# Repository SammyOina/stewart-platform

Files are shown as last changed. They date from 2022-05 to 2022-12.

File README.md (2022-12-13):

# Stewart Platform Force Balance

## Description
With the current developments around the NASA Artemis program, there has been an increased interest in the technologies around rocketry and other STEM subjects. One of the key areas around aerodynamics and specifically for this project is wind tunnel testing. Wind tunnels are commonly used in the automotive and aeronautical industries to verify mathematical model. Simulation and analysis of scaled models is an important step in the development of aircraft, vehicles and other machines since it provides aerodynamic performance data that can be used to inform any modifications or improvements. Such improvements can be aimed toward making the aircraft or vehicles more efficient or safer.

Wind tunnels simulate the behaviour of models in the presence of airflow thus allowing us to obtain the components that better define this interaction i.e. forces and moments. A force balance is consequently used in conjunction with wind tunnels to measure these these forces and moments.  Such force balances are made possible by use of sensors for data acquisition by a computer. The force balance can be 3-component or 6-component; external or internal force balance. Whereas the force balances give very accurate results, some are expensive to build and use.This is especially true in low income countries and it limits technological development in these areas.  Moreover, some objects require complex manoeuvre simulations to imitate the actual
movements in air. There is therefore the need for a solution that can achieve dynamic positioning of objects in the wind tunnel while at the same time obtaining force and moment measurements.

Our project intends to bridge this gap by the use of a low cost six degrees-of-freedom (DOF) Stewart platform as a force balance. This type of force balance will be able to position models in the wind tunnel with six degrees of freedom as well as measure six components of aerodynamic forces (drag, lift and side) and moments (pitching, rolling and yawing). The desired effect is to reduce the barrier of entry for such technology and inspire a generation of engineers who can contribute to the space and automotive industries. 

Using the Stewart platform as a force sensor requires the actuators to be locked with zero degrees of freedom. Instrumentation of the Stewart platform legs by use of strain gauges results in a force balance. Four strain gauges are attached to each leg in a Wheatstone bridge configuration, allowing the leg to act as a force sensor. There is an output every time the leg is under axial loading which is first amplified before being read. HX711s are used for analog to digital conversion of the input. Inverse kinematics is used to give various servo angles for the platform positioning. The project uses IBM cloud IoT platform to connect to our designed PCB used to control the platform and take measurements. The data is delivered to our dashboard running on IBM’s code engine which also allows us to send commands to the PCB as well. 

## What's the problem?
The high cost of wind tunnel force balances limits educational access to study areas around the scientific study in aerodynamics for aeronautical and automotive applications. Lowering the cost of force balances would increase access to studies in these fields and inspire students to participate in STEM, especially in low-income areas/countries.

## Video
[Demo video](https://youtu.be/RzLx-dEQbK0)
## Architecture 

## running
### run dashboard
`cd HMI` \
`go run main.go`

## Walkthrough

## Contributing

## Authors
- [Sammy Kerata Oina](https://www.linkedin.com/in/sammy-oina-b1774110b/)
- [Mogire Earl Spencer](https://www.linkedin.com/in/earl-spencer-b03056204//)

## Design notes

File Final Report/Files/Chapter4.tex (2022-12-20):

\section{Results and Discussion}
\subsection{Six DOF Stewart Platform}
As earlier mentioned, the Stewart platform has already been designed and fabricated and our part in this work was to do an evaluation of the same to verify its mechanical feasibility. As such, the various parts of the platform were obtained and assembled. For further analysis, a 3D model of the same platform was done using Autodesk Inventor.

The assembled Stewart platform is as shown in figure \ref{fig}. Figure \ref{fig1} shows the Stewart platform configuration setup with the Wind tunnel's test section.
\begin{center}
	\begin{figure}[H]
		\centering
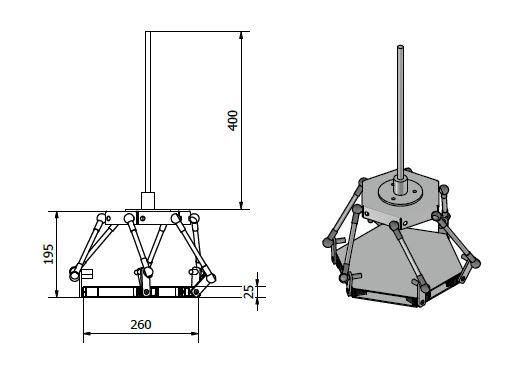
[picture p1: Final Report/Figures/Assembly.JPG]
		
		\caption[Assembled Platform]{Assembly of Stewart Platform}
		\label{fig}
	\end{figure}
\end{center}
\begin{figure}[!htb]%
	\centering
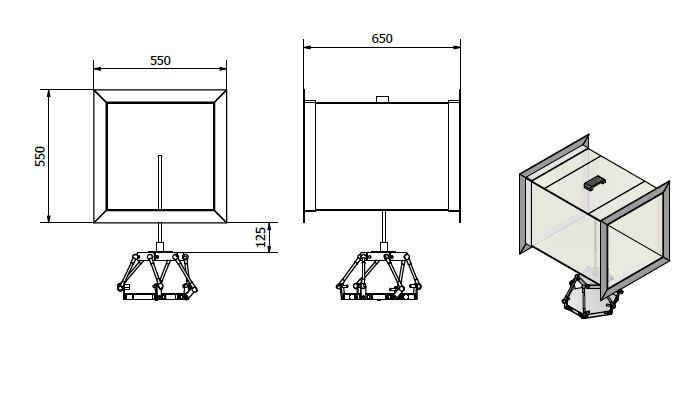
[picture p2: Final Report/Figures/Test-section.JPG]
	\subfloat[\centering Design]{{ }}%
	\qquad
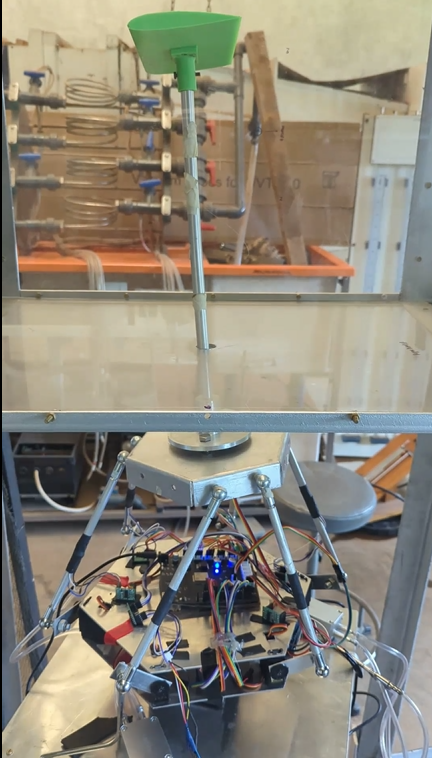
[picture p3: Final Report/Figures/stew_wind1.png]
	\subfloat[\centering Model placement in test section]{{}}
	\caption[Stewart Platform and Test Section]{Stewart platform and Test section configuration}%
	\label{fig:result}%
\end{figure}

\subsection{Strut}
Computational Fluid Dynamics was done for various values of air speed and the following drag forces were
determined from the simulations.
\begin{table}[H]
	\caption{CFD Results}
	\end{table}
	\begin{center}
	\begin{tabular}{|l|l|}
	\hline
	\textbf{Air Velocity(m/s)} & \textbf{Drag Force (N)}\\
	\hline
	10 & 1.203 \\
	\hline
	10 & 6.838 \\
	\hline
	30 & 8.068 \\
	\hline
	40 & 11.367 \\
	\hline
	\end{tabular}
\end{center}
Figure \ref{cfd} shows the effect of the strut to air flow.
\begin{center}
	\begin{figure}[H]
		\centering
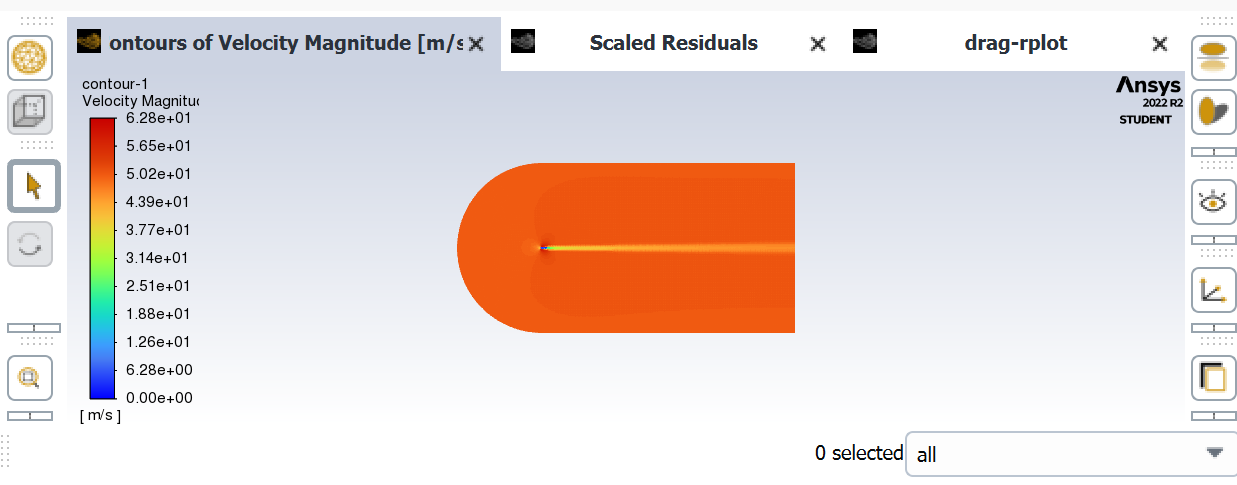
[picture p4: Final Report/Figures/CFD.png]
		
		\caption[CFD]{Computational Fluid Dynamics showing the effect of the strut to air flow}
		\label{cfd}
	\end{figure}
\end{center}

\subsection{Force Measurement by the Stewart Platform}
A static analysis test was performed and the following results were obtained:
\begin{table}[H]
	\caption{FEA Results}
\end{table}
\begin{center}
	\begin{tabular}{|l|l|l|}
		\hline
		\textbf{Name}     & \textbf{Minimum} & \textbf{Maximum} \\
		\hline
		Von Mise's        & 0 MPa            & 63.19 MPa        \\
		\hline
		Displacement      & 0 mm             & 23.74 mm         \\
		\hline
		Safety Factor     & 10.3426 ul       & 15 ul            \\
		\hline
		Equivalent Strain & 0 ul             & 0.052 ul         \\
		\hline
	\end{tabular}
\end{center}
Finite Element Analysis done showed expected strain values on each
Stewart platform leg as shown in figure \ref{strain1}.

\begin{center}
	\begin{figure}[H]
		\centering
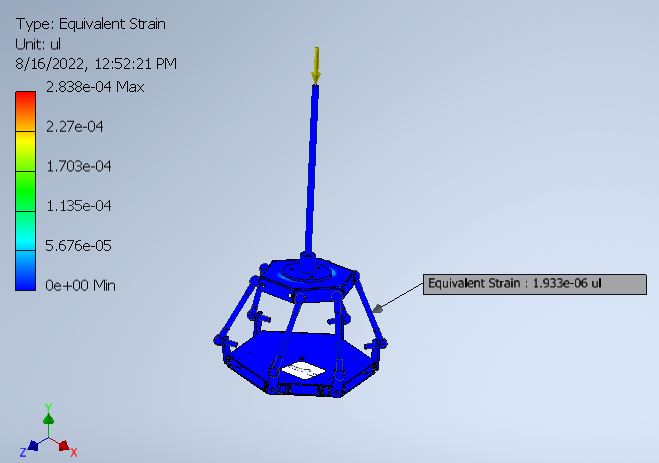
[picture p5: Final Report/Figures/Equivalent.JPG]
		
		\caption[Equivalent strain]{Strain induced on each of the legs}
		\label{strain1}
	\end{figure}
\end{center}
These strains are small and undergo amplification in order provide substantial input for the strain gauges used for force measurements.

\subsection{Human Machine Interface}
The user interface of the platform was programmed using golang and this resulted in the view below with the use of sliders for platform positioning and buttons to set model orientations and start data collection.
\begin{center}
	\begin{figure}[H]
		\centering
		
		\caption[HMI Dashboard]{HMI Dashboard}
	\end{figure}
\end{center}

The top bar of the user interface includes slider buttons to control platform orientation and commands around recording data and calibration as shown in figure \ref{fig:hmi_top}.
\begin{center}
	\begin{figure}[H]
		\centering
		
		\caption[HMI Top Bar]{HMI Top Bar}
		\label{fig:hmi_top}
	\end{figure}
\end{center}

The menu bar also provides options to test the six degrees of freedom for the whole platform as shown in figure \ref{fig:hmi_menu}.
\begin{center}
	\begin{figure}[H]
		\centering
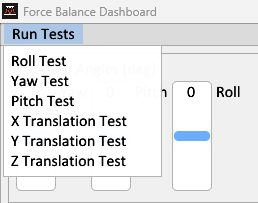
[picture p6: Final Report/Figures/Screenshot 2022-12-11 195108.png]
		
		\caption[HMI menubar]{HMI menubar}
		\label{fig:hmi_menu}
	\end{figure}
\end{center}
A calibration window is also included that is used to set the calibration factor for measurements taken as shown in figure \ref{fig:hmi_calib}
\begin{center}
	\begin{figure}[H]
		\centering
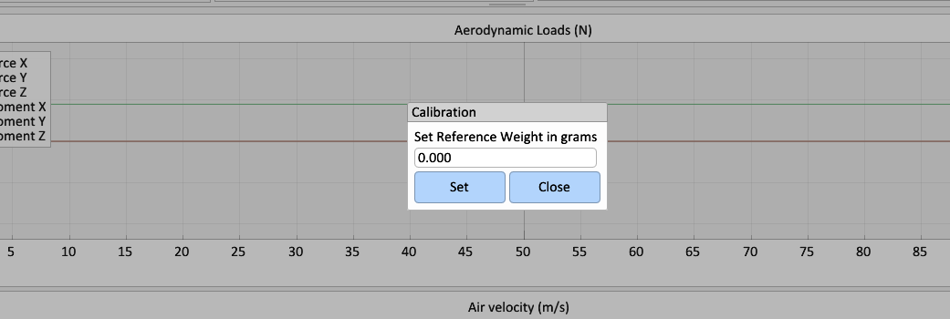
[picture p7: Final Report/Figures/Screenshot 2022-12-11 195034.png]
		
		\caption[HMI calibration]{HMI calibration}
		\label{fig:hmi_calib}
	\end{figure}
\end{center}
The incoming sensor data was also displayed on the screen as shown in the following figures:
\begin{center}
	\begin{figure}[H]
		\centering
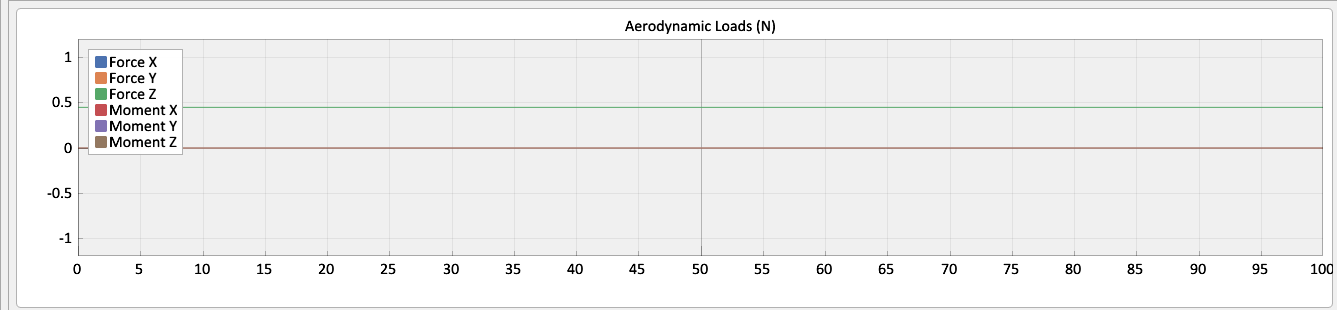
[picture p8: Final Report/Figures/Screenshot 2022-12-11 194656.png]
		
		\caption[HMI Aerodynamic loads]{HMI Aerodynamic loads}
	\end{figure}
\end{center}
\begin{center}
	\begin{figure}[H]
		\centering
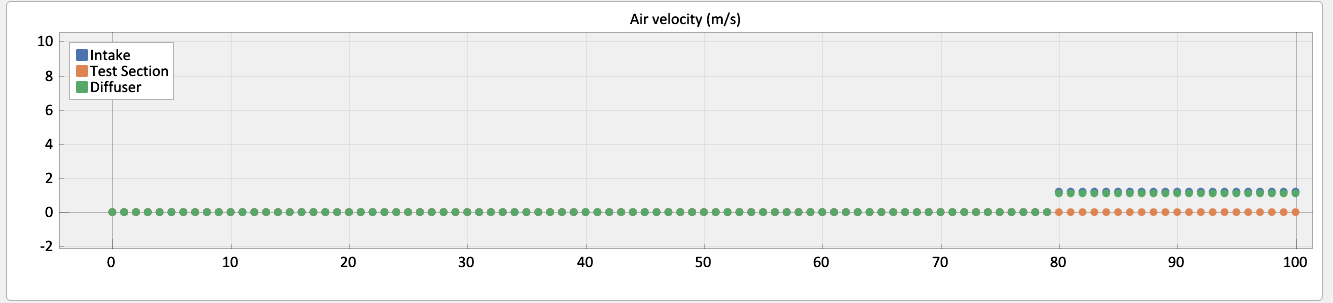
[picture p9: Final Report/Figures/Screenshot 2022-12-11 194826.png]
		
		\caption[HMI Air velocity]{HMI Air velocity}
	\end{figure}
\end{center}
\begin{center}
	\begin{figure}[H]
		\centering
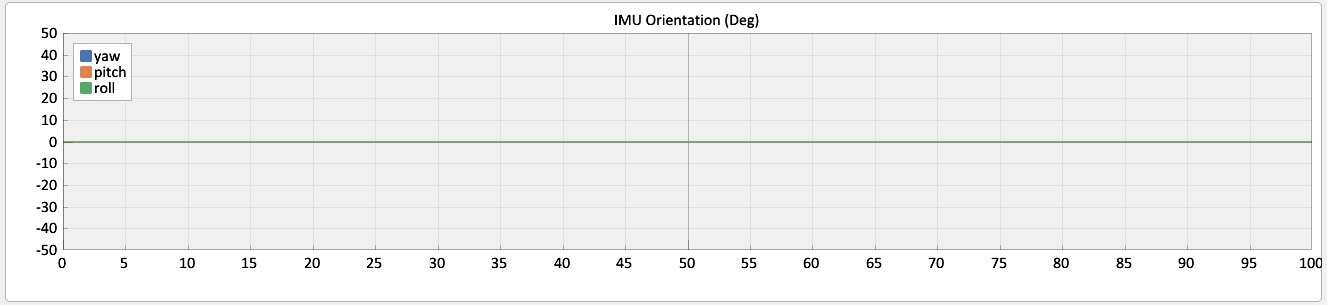
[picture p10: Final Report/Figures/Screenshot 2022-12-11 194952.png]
		
		\caption[HMI IMU readings]{HMI IMU readings}
	\end{figure}
\end{center}
\begin{center}
	\begin{figure}[H]
		\centering
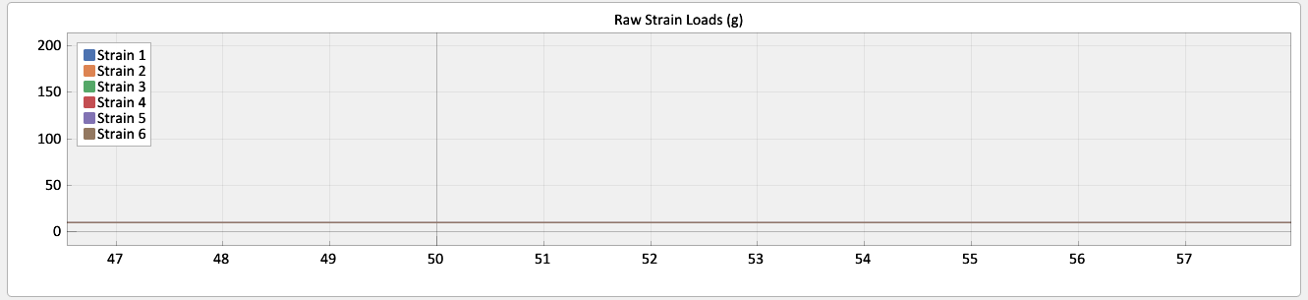
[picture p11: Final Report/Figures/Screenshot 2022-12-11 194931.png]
		
		\caption[HMI Raw Strain]{HMI Raw Strain}
	\end{figure}
\end{center}
\subsection{PCB}
The schematics from the electrical designs as seen in the appendix were routed to generate a PCB ready for manufacture. The fabricated PCB is shown in figure \ref{fig:pcb_fab}
\begin{center}
	\begin{figure}[H]
		\centering
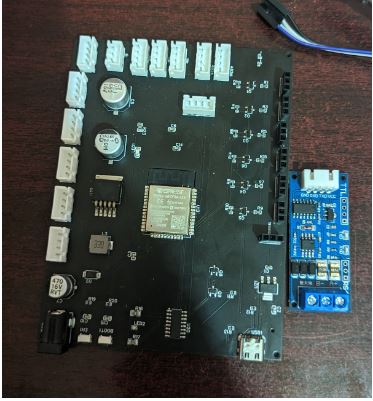
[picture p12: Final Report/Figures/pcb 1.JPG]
		
		\caption[Printed Circuit Board view]{Printed Circuit Board}
		\label{fig:pcb_fab}
	\end{figure}
\end{center}
The PCB is compact as shown in the figure \ref{fig:pcb_fab}. It is also integrates most of the components to minimize use of wires to make connections.

\subsection{Smoke Visualization}
\subsubsection{Smoke Rake}
The smoke rake was 3D printed at iPIC and assembled with its lid as shown.
\begin{figure}[!htb]%
	\centering
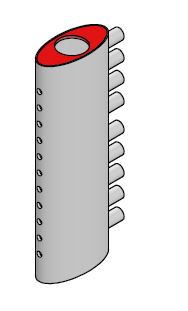
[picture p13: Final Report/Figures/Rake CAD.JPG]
	\subfloat[\centering Smoke Rake CAD]{{ }}%
	\qquad
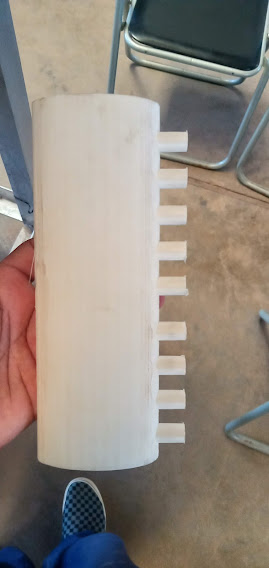
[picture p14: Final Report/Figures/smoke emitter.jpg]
	\subfloat[\centering 3D Printed Rake]{{}}
	\caption[3D Printed rake]{Smoke rake and lid assembled}%
	\label{fig:result}%
\end{figure}
\subsubsection{Smoke Rake and Pipe Assembly}
The Smoke rake was assembled with a metal pipe for rigid support and also for smoke introduction into the
smoke rake as shown.
\begin{figure}[!htb]%
	\centering
	\subfloat[\centering CAD Assembly]{{ }}%
	\qquad
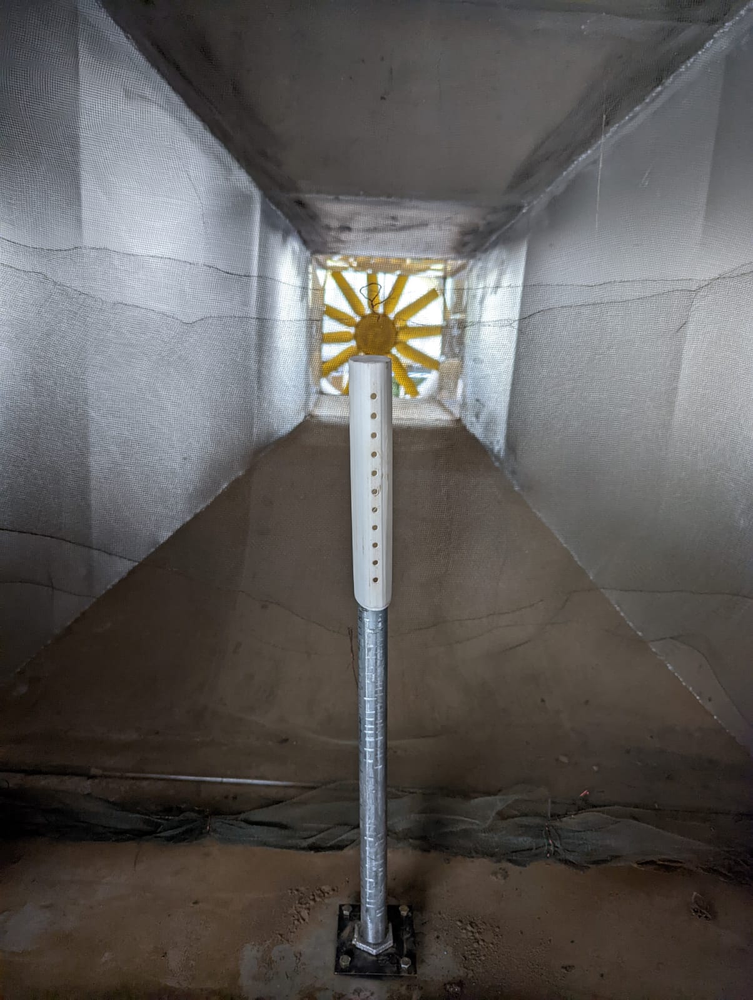
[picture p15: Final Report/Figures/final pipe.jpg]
	\subfloat[\centering Final Part]{{}}
	\caption[Final rake and pipe]{Smoke rake and pipe assembly and setup in the wind tunnel}%
	\label{fig:result1}%
\end{figure}
\subsection{Model Testing}
An aerodynamic model was subjected to wind tunnel testing and values of forces and moments were collected
using the Stewart platform force balance. The tests were done at 0 angle of attack, and at a speed of 3m/s.
The following results were obtained.
\begin{figure}[!htb]%
	\centering
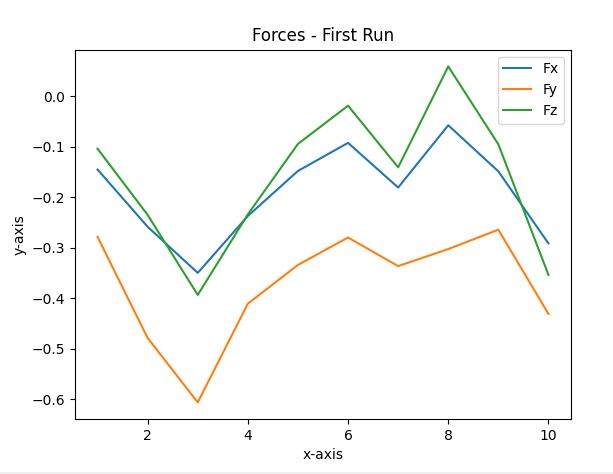
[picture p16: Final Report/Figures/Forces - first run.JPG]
	\subfloat[\centering First run]{{ }}%
	\qquad
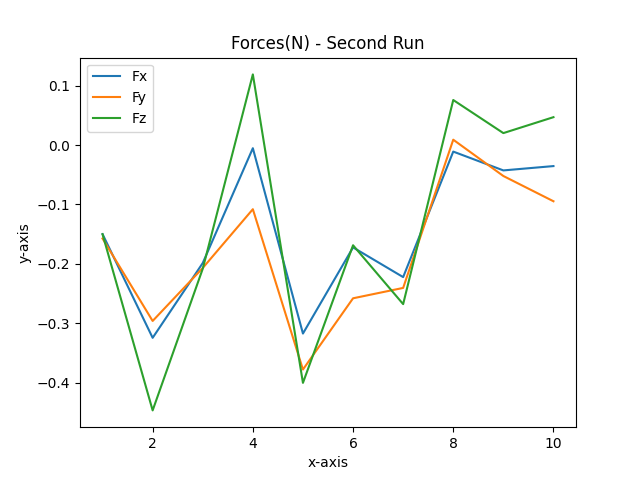
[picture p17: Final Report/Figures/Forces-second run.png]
	\subfloat[\centering Second run]{{}}
	\caption[Force values for first and second run]{Force values for first and second run}%
	\label{fig:result1}%
\end{figure}
\begin{center}
	\begin{figure}[H]
		\centering
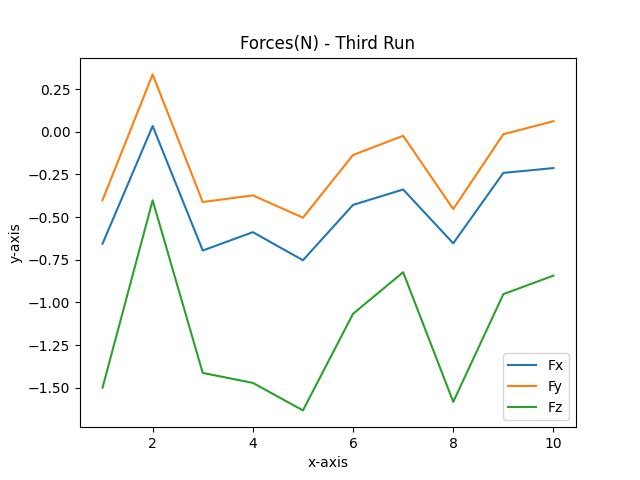
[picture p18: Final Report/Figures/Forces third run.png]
		
		\caption[Forces Third run]{Forces obtained form the third run}
		\label{fig:pcb_fab}
	\end{figure}
\end{center}
%\begin{figure}[!htb]%
%	\centering
%	\subfloat[\centering First run]{{\includegraphics[width=8cm]{Figures/Moments_first_run.png} }}%
%	\qquad
%	\subfloat[\centering Second run]{{\includegraphics[width=8cm]{Figures/Moments_second_run.png}}}
%	\caption[Moment values for first and second run]{Moment values for first and second run}%
%	\label{fig:result1}%
%\end{figure}
%\begin{center}
%	\begin{figure}[H]
%		\centering
%		\includegraphics[width=0.7\linewidth]{Figures/Moments third run.png}
%		\caption[Moments from Third run]{Moments obtained form the third run}
%		\label{fig:pcb_fab}
%	\end{figure}
%\end{center}
\subsection{Discussion}
The Stewart platform is able to position models in various dynamic positions depending on the angle values
of yaw, roll and pitch as well as the amount of displacements in the x-, y- and z-directions input via the HMI.
 Application of load on the platform
subjects each of the legs to axial forces which causes strain. This strain can be used to determine aerodynamic forces
on models during wind tunnel testing. However, aerodynamic forces due to the strut must be put to account because from
simulations, drag forces are developed by the strut when there is airflow. Smoke introduced into the wind tunnel allows
visualization of airflow around a model. Pitot tube probes used and their transducers provide valuable information used 
in post analysis to determine the aerodynamic coefficients (drag, lift).

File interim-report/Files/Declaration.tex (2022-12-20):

\addcontentsline{toc}{section}{Declaration}
\section*{Declaration}

We hereby declare that the work contained in this report is original; researched and documented by the undersigned students. It has not been used or presented elsewhere in any form for award of any academic qualification or otherwise. Any material obtained from other parties have been duly acknowledged. We have ensured that no violation of copyright or intellectual property rights have been committed.
\begin{enumerate}
	\item Sammy Kerata Oina\vspace*{.2cm}\\
	Signature\ldots\ldots\ldots\ldots\ldots\ldots\ldots\ldots\ldots\ldots Date\ldots\ldots\ldots\ldots\ldots\ldots\ldots\ldots\ldots\ldots
	\item Earl Spencer Mogire\vspace*{.2cm}\\
	Signature\ldots\ldots\ldots\ldots\ldots\ldots\ldots\ldots\ldots\ldots Date\ldots\ldots\ldots\ldots\ldots\ldots\ldots\ldots\ldots\ldots
\end{enumerate}

\vspace*{.5cm}
Approved by supervisors:
\begin{enumerate}
	\item Dr. Anthony K. Muchiri \vspace*{.2cm}\\
	Signature\ldots\ldots\ldots\ldots\ldots\ldots\ldots\ldots\ldots\ldots Date\ldots\ldots\ldots\ldots\ldots\ldots\ldots\ldots\ldots\ldots
	%\item Prof. George N. Nyakoe\vspace*{.2cm}\\
	%Signature\ldots\ldots\ldots\ldots\ldots\ldots\ldots\ldots\ldots\ldots Date\ldots\ldots\ldots\ldots\ldots\ldots\ldots\ldots\ldots\ldots
	%\item Ms. Maurine Andanje\vspace*{.2cm}\\
	%Signature\ldots\ldots\ldots\ldots\ldots\ldots\ldots\ldots\ldots\ldots Date\ldots\ldots\ldots\ldots\ldots\ldots\ldots\ldots\ldots\ldots
\end{enumerate}

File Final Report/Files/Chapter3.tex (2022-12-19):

\section{Methodology}
\subsection{Outline}
This section will look into:
\begin{itemize}
	\item Mechanical Design:
	\item Electrical Design
	\item Instrumentation
	\item Software and Control Design
\end{itemize}

\subsection{Mechanical Design}
\subsubsection{Inverse Kinematics of a Stewart Platform}
This is the calculation of each leg length based on the desired position of the Stewart platform.
For the Stewart platform, the translation $^{p}T_{b}$ from the base origin to the platform origin can be described with a single vector T = $(t_{x} t_{y} t_{z})^{T} $. The rotation of the platform can be denoted as $^{p}R_{b}$. Thus the following relationship for the frame of reference can be stated \cite{Eisele_2019}:
\begin{ceqn}
	\begin{align}
		^{p}T_{b} = T
	\end{align}
\end{ceqn}
\begin{ceqn}
	\begin{align}
		^{p}R_{b} = R
	\end{align}
\end{ceqn}
\begin{ceqn}
	\begin{align}
		^{b}T_{p} =(^{p}T_{b})^{-1} =T^{-1}
	\end{align}
\end{ceqn}
\begin{ceqn}
	\begin{align}
		^{b}R_{p} = (^{p}R_{b})^{-1}
	\end{align}
\end{ceqn}
\begin{center}
	\begin{figure}[!h]
		\centering
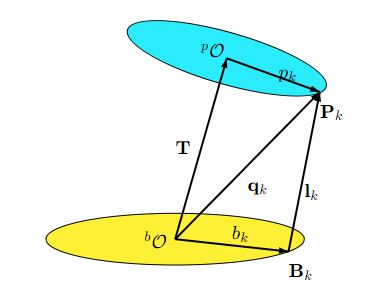
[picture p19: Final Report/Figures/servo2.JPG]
		
		\caption[Leg length]{Leg Length \cite{Eisele_2019}}
	\end{figure}
\end{center}
The leg length $l_{k}$ can therefore be found with:
\begin{ceqn}
	\begin{align}
		l_{k} = P_{k} - B_{k} = T + R \times p \times R^{-1} - b_{k}
	\end{align}
\end{ceqn}
Where,\\
$P_{k}$ - leg attachment on platform \\
$B_{k}$- leg attachment on base
\subsubsection{Inverse Kinematics Using Rotational Servo Motors}
For a rod of fixed length d between servo horn anchor $H_{k}$ and platform anchor $P_{k}$.  $H_{k}$ has a distance h between the original base anchor and servo shaft $B_{k}$. The vector h is perpendicular to the servo shaft and is rotated by angle $\alpha_{k}$ when lifted from the horizontal line.
\begin{center}
	\begin{figure}[!h]
		\centering
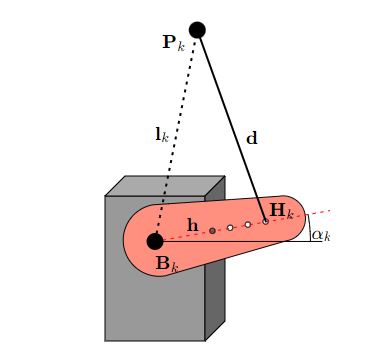
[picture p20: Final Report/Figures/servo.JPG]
		
		\caption[Servo angle]{Servo angle \cite{Eisele_2019}}
	\end{figure}
\end{center}
Further, looking from the top onto the base, each servo can be rotated by the angle $\beta_{k}$ in addition to its position $B_{k}$. The servo shaft $s_{k}$ moves in the x-y plane and is orthogonal to the vector h.
\begin{center}
	\begin{figure}[!h]
		\centering
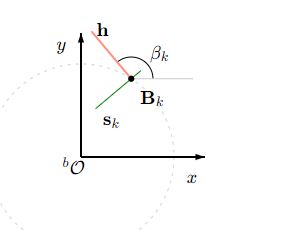
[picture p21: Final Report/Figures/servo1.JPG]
		
		\caption[Planar view]{Planar view \cite{Eisele_2019}}
	\end{figure}
\end{center}
The anchor $H_{k}$ can be calculated as we rotate around the z-axis with angle $\beta_{k}$ and  by $-\alpha_{k}$ around the y-axis to lift the servo horn which lies in the local x-axis \cite{Eisele_2019}.
\begin{ceqn}
	\begin{align}
		H_{k} = B_{k} + R_{z}(\beta_{k}) R_{y}(-\alpha_{k})\begin{pmatrix}
			                                                   |h| \\ 0 \\ 0
		                                                   \end{pmatrix}
		\label{eq:myeqn2}
	\end{align}
\end{ceqn}
\begin{ceqn}
	\begin{align}
		= B_{k} + |h|\begin{pmatrix}
			             cos(\alpha_{k})cos(\beta_{k}) \\
			             cos(\alpha_{k})sin(\beta_{k}) \\
			             sin(\alpha_{k})
		             \end{pmatrix}
		\label{eq:myeqn4}
	\end{align}
\end{ceqn}
Carrying out the same procedure but with the servo arm when it is on the opposite side and we have:
\begin{ceqn}
	\begin{align}
		H_{k} = B_{k} + R_{z}(\beta_{k}) R_{y}(\pi -\alpha_{k})\begin{pmatrix}
			                                                       -|h| \\ 0 \\ 0
		                                                       \end{pmatrix}
		\label{eq:myeqn5}
	\end{align}
\end{ceqn}
\begin{ceqn}
	\begin{align}
		= B_{k} + |h|\begin{pmatrix}
			             cos(\alpha_{k})cos(\beta_{k}) \\
			             cos(\alpha_{k})sin(\beta_{k}) \\
			             sin(\alpha_{k})
		             \end{pmatrix}
		\label{eq:myeqn6}
	\end{align}
\end{ceqn}
Squaring the lengths of h, d, $l_{k}$ we get the relationship:
\begin{ceqn}
	\begin{align}
		h^2 = (H_{k}-B_{k})^{T}(H_{k}-B_{k})
	\end{align}
\end{ceqn}
\begin{ceqn}
	\begin{align}
		d^2 = (P_{k}-H_{k})^{T}(P_{k}-H_{k})
	\end{align}
\end{ceqn}
\begin{ceqn}
	\begin{align}
		l_{k}^2 = (P_{k}-B_{k})^{T}(P_{k}-B_{k})
	\end{align}
\end{ceqn}
From the above relationships, further derivation and trigonometric substitutions are done to obtain the inverse kinematics used to calculate each servo angle. This is given as \cite{Eisele_2019}:
\begin{ceqn}
	\begin{align}
		\alpha_{k} = sin^{-1}(\frac{g_{k}}{\sqrt{e_{k}^2+f_{k}^2}})-arctan2(f_{k}, e_{k})
	\end{align}
\end{ceqn}
Where,
$$e_{k} = 2hl_{k}^{(z)} $$
$$e_{k} = 2h(cos(\beta_{k})I_{k}^{(x)}+sin({\beta_{k}})I_{k}^(y))$$
$$g_{k} = l_{k}^2 - (d^2 - h^2)   $$

\subsubsection{Actuation}
Two methods of actuation are popular with Stewart platforms:
\begin{itemize}
	\item Linear actuators
	\item Use of motors
\end{itemize}
Whereas linear actuators are relatively easy to control, they are very expensive. Thus the choice of motors.

\subsubsection*{Motor Selection}
One parameter was considered in our motor selection i.e. torque required. From the Autodesk Inventor design environment, the mass of the moving platform and mechanical couplings was 2.6kg. Each motor is supposed to move a minimum mass of 0.177kg. Using a servo horn of distance 45mm centre-to-centre, and Distance = $ \pi $ D, then:
\begin{ceqn}
	\begin{align}
		Torque = (0.1777 \times 9.81)\times \frac{141.37}{1000} = 0.246 N\cdot m
	\end{align}
\end{ceqn}
Motors of minimum torque of 0.2 N $\cdot m$ were considered. But for control considerations, only stepper motors and servo motors were shortlisted. Servo motor was considered over Stepper motor because they are cheaper. Also, we are only interested in 0 - 180 degrees positions.

The Servo motor \textbf{TowerPro MG995} is suitable for this project. The specifications provided by the manufacturer are as follows:

\begin{table}[!h]
	\caption[Motor Specifications]{TowerPro MG995 Specifications}
\end{table}
\begin{center}
	\begin{tabular}{|l|l|}
		\hline
		\textbf{Model}                  & TowerPro MG995                \\
		\hline
		\textbf{Operating Voltage}      & 4.8V - 6.6V                   \\
		\hline
		\textbf{Operating Speed @ 4.8V} & 0.20sec/60$^{\circ}$          \\
		\hline
		\textbf{Operating Speed @ 6.6V} & 0.16sec/60$^{\circ}$          \\
		\hline
		\textbf{Stall torque @ 4.8V}    & 9.4 kg-cm or 0.94 N $\cdot$ m \\
		\hline
		\textbf{Stall torque @ 6.6V}    & 11 kg-cm or 1.1 N $\cdot$ m   \\
		\hline
	\end{tabular}
\end{center}
Prices range between \textbf{Ksh.700} and \textbf{Ksh.1400}

The previous servos used for the project were SG5010 which proved not to be able to handle the torque requirements of the platform,
as a result the plastic gears in those servos were destroyed. The replacement of the servos with MG995 solved the problem due to the higher torque capacity and has metal gears.

\subsubsection{Finite Element Analysis}
A Finite Element Analysis was done on the Stewart platform design to determine its performance under given loads. The platform is going to be subjected to a force during wind tunnel testing. A maximum load of 50N was selected for the Finite Element Analysis. This could be more or less since models vary in size. The z-component of the force is considered.
The mesh generated is shown in the figure \ref{fig:feamesh}.
\begin{center}
	\begin{figure}[H]
		\centering
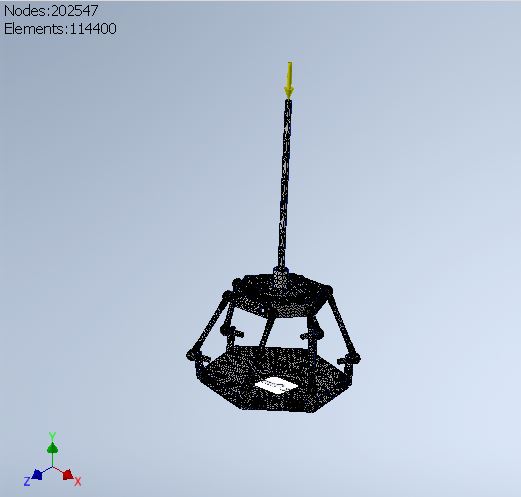
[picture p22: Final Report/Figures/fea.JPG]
		
		\caption[Stewart platform mesh]{Stewart platform mesh}
		\label{fig:feamesh}
	\end{figure}
\end{center}
The rods/legs of the Stewart platform were subjected to axial forces which caused slight strains which can be used to obtain force and moment measurements during wind tunnel testing.
\clearpage
\begin{center}
	\begin{table}[H]
		\caption{Operating Conditions}
		\centering
	\end{table}
	\begin{tabular}{|l|l|}
		\hline
		\textbf{Load Type} & \textbf{Force} \\
		\hline
		Magnitude          & 50.0N          \\
		\hline
		Vector X           & 7.794N         \\
		\hline
		Vector Y           & -48.206N       \\
		\hline
		Vector Z           & 10.745N        \\
		\hline
	\end{tabular}
\end{center}

\begin{center}
	\begin{table}[!h]
		\caption[FEA Setup]{Other FEA setup parameters}
		\centering
	\end{table}
	\begin{tabular}{|l|l|}
		\hline
		Constraint & Fixed                       \\
		\hline
		Materials  & Aluminium 6061              \\
		           & Stainless steel             \\
		\hline
		Contacts   & All bonded                  \\
		\hline
		Mesh       & Avg element size: 0.1mm     \\
		           & Minimum element size: 0.2mm \\
		           & Grading Factor: 1.50        \\
		           & Maximum turn angle: 60 deg  \\
		\hline
	\end{tabular}
\end{center}

\subsection{Strut}
The strut will go into the test section of the Wind tunnel. Consequently, it will be
subjected to the flow forces in the wind tunnel. It has therefore been made of as small diameter as possible.
A computational fluid dynamics test was done to ascertain the magnitude of drag force experienced and the effect that the strut
will have on the flow in the tunnel. The test was done using ANSYS.
\begin{center}
	\begin{table}[!h]
		\caption[CFD Setup]{CFD setup parameters}
		\centering
	\end{table}
	\begin{tabular}{|l|l|}
		\hline
		\textbf{Parameter} & \textbf{Value/Type} \\
		\hline
		Type of test       & Fluid flow (Fluent)         \\
		\hline
		Type of Simulation & Steady State\\
		\hline
		Type of fluid      & air                 \\
		\hline
		Mesh size      &  0.001mm            \\
		\hline
		Growth rate     & default (1.2)             \\
		\hline
		Behavior  & soft             \\
		\hline
		Defeature size      & 5.5902 e-004m               \\
		\hline
		Velocity           & 10 - 40 m/s         \\
		\hline

	\end{tabular}
\end{center}
The speed of air flow in the wind tunnel is variable thus the simulation was done 
using speeds between 10m/s and 40 m/s in steps of 10 m/s.

\subsubsection{Smoke Visualization System}
To implement streamline smoke lines in the wind tunnel, a smoke rake, which is an aerodynamically shaped
body (usually elliptical) featuring a row of tubes through which the smoke exits was designed.
The CAD model was deigned using Autodesk Inventor and the rake was prepared for 3D printing at iPIC
in JKUAT. The rake design is shown in figure \ref{smoke}.
\begin{center}
	\begin{figure}[H]
		\centering
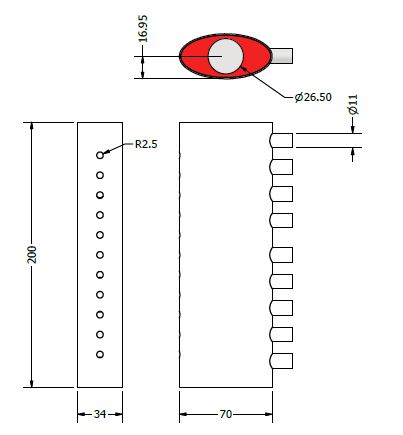
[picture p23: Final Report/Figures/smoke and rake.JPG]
		
		\caption[Smoke Rake]{Smoke rake design}
		\label{smoke}
	\end{figure}
\end{center}
The smoke emitting holes are 6mm in diameter and the air inlet holes are 5mm in diameter.
20mm diameter hole on the lid (color coded red) shown in the  plan view is for metal pipe connection.

\subsubsection*{Smoke Rake and Pipe Assembly}
A metal pipe was used to provide rigid support to the smoke rake in the wind tunnel as well as placing it at the center
(vertically). A pipe of length 400mm and diameter 3/4"(19.05mm) is used. The pipe surface was roughed using a hacksaw in
order to minimize any turbulence in the flow since it was be placed in the intake section. A 1.5mm plate of 10mm by 10mm by
and two plumbing nuts are required to mount the pipe in the intake section. The smoke rake and pipe design is shown
in figure \ref{pipe and rake}
\begin{center}
	\begin{figure}[H]
		\centering
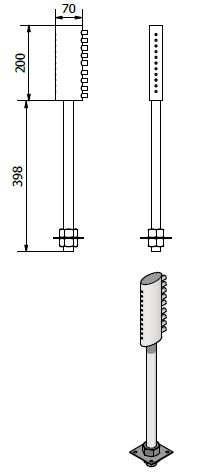
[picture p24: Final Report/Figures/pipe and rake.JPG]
		
		\caption[Pipe and rake]{Pipe and rake assembly design}
		\label{pipe and rake}
	\end{figure}
\end{center}
For the complete assembly, a 20mm diameter hole was drilled on the floor of the wind tunnel at the intake section
and the pipe was held fast to the floor by two plumbing nuts on both sides of the 1.5mm plate. The plate was fastened to
the floor by use of M6 bolts and nuts.
\subsection{Instrumentation}
\subsubsection{Design of the Force Sensor}
The force sensor module was used to measure the force and moments from the aerodynamic loads applied on model 
being tested in the wind tunnel. The forces to be measured are the drag, lift and thrust as well as
 associated moments. For this subsystem two possible conceptual designs were considered:
\begin{itemize}
	\item External force sensor
	\item Stewart Platform as a force sensor
\end{itemize}
\subsubsection*{External Force Sensor}
In this case it would require at least 3 orthogonally positioned load cells measuring each force component. Each load cell would be mechanically linked to the model such that forces experienced on each axis are measured by each load cell as shown in figure \ref{fig:balex}.
\begin{center}
	\begin{figure}[H]
		\centering
		
		\caption[Diagram of a force balance]{Diagram of a force balance \cite{post_force_2010}}
		\label{fig:balex}
	\end{figure}
\end{center}
This configuration is, however, bulky since it requires an additional external system for force measurements in addition to the Stewart platform for positioning the model. This is however complemented by the simplicity in calibration of the load cells and does not require a complex force transformation matrix and other issues with force amplification created by the use of an integrated system.
\subsubsection*{Stewart Platform as a force sensor}
In this configuration, the Stewart platform legs are used as force sensors by attaching strain gauges on the 
legs of platform. Similar work has been done by Ferreira\cite{ferreira2015design} without the use of actuators as is proposed in this project. Using the Stewart platform as a force sensor requires the actuators to be locked with zero degrees of freedom.

Four strain gauges are required for each leg for a full Wheatstone bridge configuration.
\begin{center}
	\begin{figure}[H]
		\centering
		
		\caption[Strain Gauge Configuration]{Strain Gauge Configuration \cite{noauthor_measuring_nodate}}
		\label{strain}
	\end{figure}
\end{center}
In this case, as shown in figure \ref{strain}, the load cells are able to measure the axial strain on each leg. R1 and R3 are active strain gauges measuring the compressive Poisson effect (–νe). R2 and R4 are active strain gages measuring the tensile strain (+e). The output generated from the Wheatstone bridge is then amplified and read to determine the strain on each leg.
In the case of this project, a full bridge strain gauge sensor with each strain gauge orthogonally positioned allowing for elimination of noise and measurement of the strain axially on each rod is used.

\subsubsection*{Force transformation matrix}
The forces experienced at the top of the platform are distributed between the 6 legs and as result, a force transformation matrix is required to resolve the forces applied on each axis as measured by each load cell on each leg.

The forces experienced by the legs can be expressed as:
\begin{ceqn}
	\begin{align}
		\begin{Bmatrix}
			\vec{F}_e \\
			\vec{M}_e \\
		\end{Bmatrix} = [H]\{F\}
	\end{align}
\end{ceqn}

Where
\begin{itemize}
	\item $\vec{F}_e $ - external force applied to the platform
	\item $\vec{M}_e$ - external moment applied to the platform
	\item H - transformation matrix which relates measured forces and applied forces
	\item F - axial force
\end{itemize}
The derivation has been done and is presented in the appendix A.4.

\subsubsection*{Bonding strain gauges}
The strain gauge bonding process began by roughing the bonding surface on the aluminium tubes using sand paper. 
The surface was then cleaned using acetone. Superglue was when applied on the surface followed by the strain gauge while applying pressure on the strain gauge. 
Resin (araldite) was then placed on the strain gauge to provide protection to strain gauge from mechanical damage. 
Jumper wires were then soldered onto the lead wires of the strain gauge as shown in \ref{fig:strain_bond}. 
Finally, the assembly was covered with heat shrinkable tubing.
\begin{center}
	\begin{figure}[H]
		\centering
		
		\caption[Strain gauge bonding process]{Strain gauge bonding process}
		\label{fig:strain_bond}
	\end{figure}
\end{center}

\subsection{Velocity Measurement}
An important part in wind tunnel measurements is the measure of pressure at specific points in the wind tunnel and computing the corresponding air speed. This is achieved by the use of a pitot probe.
\begin{center}
	\begin{figure}[H]
		\centering
		
		\caption[Pitot-static tube]{Pitot-static tube \cite{viquerat_continuous_2006}}
	\end{figure}
\end{center}
For steady flow of an incompressible fluid for which viscosity can be neglected, the fundamental equation has the form\cite{viquerat_continuous_2006}:

\begin{ceqn}
	\begin{align}
		v = \sqrt{\frac{2(P_{0} - P)}{\rho}}
	\end{align}
\end{ceqn}

Where V is the speed of the fluid, $P_{0}$ is the total, also called the stagnation, pressure at that point of measurement, and P is the static pressure at the same point.

\begin{center}
	\begin{figure}[H]
		\centering
		
		\caption[RS485 communication]{RS485 communication}
		\label{fig:rs485}
	\end{figure}
\end{center}
The module communicates to the microcontroller using a TTL to RS485. Each module is individually addressable further simplifying the interface as shown in figure \ref{fig:rs485}.
The protocol allows for long distance serial communication and interface with multiple devices on the same bus.

Three pitot probes were setup in the wind tunnel i.e. in the test section, intake and diffuser sections.
\begin{center}
	\begin{figure}[H]
		\centering
		
		\caption[Pitot setup]{Pitot setup in the intake and diffuser}
		\label{pitot loc}
	\end{figure}
\end{center}
Pitot location in the intake is exactly at the beginning of the test section and pitot location in the diffuser
is exactly at the end of the test section as shown in figure \ref{pitot loc}.

\subsection{Electrical Design}
This section looks at the required electrical connections to make the system functional and interface with the control unit.
\subsubsection{Printed Circuit Board Design}
This section looks at the design of the circuits used to power and get readings from the sensors and control the actuators.

\subsubsection{Microcontroller}
The main requirement for this was the need for wireless communication via WIFI and large number of I/O interface
 at cost effective rate. This brought down the options to the ESP32 and Raspberry Pi RP2040. Both are dual core devices
  which are feature rich. However, the raspberry rp2040 only has 28 I/O pins while the ESP32 has 34 pins and due to this
   the ESP32 was chosen.
\begin{center}
	\begin{figure}[H]
		\centering
		
		\caption[Microcontroller]{Microcontroller}
	\end{figure}
\end{center}
\subsubsection{Power Supply}
The power supply chosen is an AC/DC power converter since the highest voltage required is 12 volts. This is also used as the highest power supply to the PCB.

Both 5 and 3.3 volts are required in the PCB for other peripherals. To this end, a buck converter and linear converter are used for 5 ad 3.3 volts respectively.

\begin{center}
	\begin{figure}[H]
		\centering
		
		\caption[Buck converter]{Buck Converter 12V to 5V}
	\end{figure}
\end{center}

\begin{center}
	\begin{figure}[H]
		\centering
		
		\caption[Linear Voltage Converter]{Linear level converter 5V to 3.3v}
	\end{figure}
\end{center}
The linear converter dissipates the energy loss though heat while buck converter is through switching.

\subsubsection{Servo Control}
Since the microcontroller used (ESP32) is based on 3.3V logic, there is a need for 5V logic to control the servos and thus a bidirectional logic level converter was utilized which leverages an internal drain N-channel MOSFET.
\begin{center}
	\begin{figure}[H]
		\centering
		
		\caption[Bidirectional Logic Level converter]{Bidirectional Logic Level converter}
		\label{fig:logik}
	\end{figure}
\end{center}
The configuration designed is shown in figure \ref{fig:logik}

\subsubsection{Force measurement Circuit}

The output excitation of the Wheatstone bridge needs to be amplified as it results in low outputs. An analogue to digital converter is also required for the analogue to digital converter. Some considerable options were the HX711 or the AD7193 converters which may be used as digital to analogue converters. The AD7193 is designed for high precision and has a delta sigma filter to remove noise from measurements.  
However, the AD7193 was not used due to it's high cost compared to the HX711 regardless of the advantage it offers with serial peripheral Interface communication allowing for multiple modules on the same bus.

The connection of the AD7193 to the microcontroller is via Serial Peripheral Interface (SPI). The configuration is as shown in figure \ref{spi}:
\begin{center}
	\begin{figure}[H]
		\centering
		
		\caption[SPI configuration]{SPI configuration}
		\label{spi}
	\end{figure}
\end{center}
In this configuration the when the chip select pin of an amplifier is set to low, the microcontroller is able to obtain data from that strain gauge. This configuration allows for a four wire interface to connect to six strain gauge sensors and obtain measurements.

The HX711 however allows for the I2C like communication via two wires (serial clock (SCL) and Serial Data (SDA)). They, however, do not have hardware addresses thus many pins are required for the interface. This can however be remedied by the use of a shared SCL between each of the amplifier modules reducing the overall number of pins required to interface.

\subsection{Software and Control}
This section deals with the control of the Stewart platform. It involves allowing input and obtaining output form the platform force balance.
\subsubsection{Human Machine Interface}
The purpose of the interface is to enable control of the platform position as well as to obtain measured data from the strain gauges and pitot tubes.
The general layout is as shown in the figure \ref{fig:hmi}:
\begin{center}
	\begin{figure}[H]
		\centering
		
		\caption[Human Machine Interface]{Human Machine Interface}
		\label{fig:hmi}
	\end{figure}
\end{center}

The primary interface between the microcontroller is wireless.
For this interface two transport methods were considered: User Datagram Protocol (UDP) and Transmission Control protocol (TCP).
UDP is a communications protocol that is primarily used to establish low-latency and loss-tolerating connections.
TCP on the hand does not experience data loss and in our case the use of protocol buffers as a means of serialization of messages to binary saving on bandwidth.
TCP requires only one initial handshake between the server and client, after which messages can be transmitted continuously (streaming).
Due to assurance of data integrity (no loss) and lower bandwidth use thus higher data transfer rates, TCP was chosen as the main protocol.
This allows for high speed low latency communication without need for a wired connection. It also allows for bidirectional streaming of information thus allowing for both control input and output of measured values. The interface is to enable the abstraction of data acquisition and actuator control to a simple interaction with buttons and other visual interfaces available in a computer program.
The decoupling of the microcontroller and the program to be hosted on the desktop allows for advanced data processing such as application of filters and resolving measurements into usable information. It also allows for the use of more powerful processor and high level programming languages to more effectively perform complex calculations without taking a toll the sensor sampling rate that would occur with on board processing in the microcontroller.

A user interface was also required to record user input and display incoming data.
\subsubsection{Control Algorithm}
\begin{center}
	\begin{figure}[H]
		\centering
		
		\caption[Control Algorithm]{Control Algorithm for the Stewart Platform with Force Measurement}
	\end{figure}
\end{center}

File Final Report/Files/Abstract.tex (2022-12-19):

% !TeX spellcheck = en_GB
\addcontentsline{toc}{section}{Abstract}

\section*{Abstract}
\label{sec:Abstract}
Aerodynamic analysis of the performance of models within a wind tunnel is an important step in the design and development of vehicles and aircraft. Wind tunnel testing provides a way of verifying data collected from simulations.
There is, however, need to orient models during testing, which is accomplished in this project by the use of a Stewart platform.

The Stewart platform force balance was designed to orient models with six degrees of freedom based on inverse kinematics
as well as to measure 6 components of forces and moments based on strain gauge sensors. 
A human machine interface dashboard was consequently created to allow control of the platform orientation and display of measurement results. Three dimensional models of the platform were created using Autodesk Inventor to show the configuration allowing for six degrees based on the inverse kinematic equations. 
Additonally, pitot tubes were setup in different locations in the wind tunnel and were used measure air velocity. Further,
a smoke distribution assembly was incorporated in the wind tunnel to aid in visualizing the interaction
of test models with the airflow. A printed circuit board to be used was also designed using Easy EDA and was fabricated. 

The force balance ws tested in the wind tunnel with a model aerofoil to verify its operation. Durng the test,
the platform orientation could be controlled via the dashboard, measurements were obtained and use of smoke 
streamlines improved visualization of model interaction with the airflow.

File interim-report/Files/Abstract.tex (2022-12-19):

% !TeX spellcheck = en_GB
\addcontentsline{toc}{section}{Abstract}

\section*{Abstract}
\label{sec:Abstract}
Aerodynamic analysis of the performance of models within a wind tunnel is an important step in the design of vehicles and aircraft. It is important to measure the aerodynamic performance in metrics such as drag and lift in comparison to simulations during design.
Due to the complex manoeuvres that may require simulation, there is a need for dynamic positioning of the model of the object in the wind tunnel. As a result, the design of a Stewart platform force balance to replicate these complex manoeuvres during wind tunnel tests as well as to position the model to obtain the required data.

The modelling, simulation and development of a Stewart platform
based force balance for a low speed wind tunnel will be covered in this work.
Modelling and simulation of the kinematics of the Stewart platform was done using MATLAB along with a simulation to visualize the movements. 
The human machine interface dashboard was also created to allow interaction with the platform. The printed circuit board to be used was also designed using Easy EDA and was fabricated. Three dimensional models of the platform were created using Autodesk Inventor to show the configuration allowing for six degrees of freedom which was verified by the simulation on MATLAB.

Finally, an already existing model was tested in the wind tunnel to evaluate the performance
of the platform. The platform was able to position the test
item and measure aerodynamic loads while pitot tubes were positioned in the wind tunnel to measure air velocity.
Further, a smoke visualization assembly was incorporated into the wind tunnel to improve visualization of the model 
interaction with the airflow.
 Data logging of the obtained measurements will be done using a bespoke computer program for further analysis.

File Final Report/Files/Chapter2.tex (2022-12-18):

\section{Literature Review}
\subsection{Wind Tunnel}
A wind tunnel is a large tube with air moving inside. This movement of air is usually done by powerful fans.
\begin{center}
	\begin{figure}[H]
		\centering
		
		\caption[A Typical Wind Tunnel]{Diagram of a typical wind tunnel \cite{morris_force_2010}}
	\end{figure}
\end{center}
The first wind tunnel was built by Francis Wenham in 1871. However, it was the Wright Brothers who were the first to show the value of the wind tunnel in aerodynamic design with their 1902 wind tunnel. The Wright Brothers’ wind tunnel was largely made of wood, with a glass window on the top to look down through and see the force balance, from which the
lift and drag forces could be read. The wind tunnel was powered by a fan driven off a natural gas fuelled engine. Their tunnel was square of 16" by 16"(about 407mm by 407mm), and 6 foot long (about 1829mm), with a maximum test speed of 35 mph (about 56 km/h)\cite{morris_force_2010}.

Later in the early 20th century in Europe, the main users of wind tunnels were Gustave Eiffel in France and Ludwig Prandtl in Germany. Prandtl built the first closed circuit wind tunnel in 1908. Closed circuit wind tunnels are characterized by the recirculation of the airflow with very minimal exchange with the exterior. Open circuit wind tunnels on the other hand, have an airflow that follows a straight path and flows to the contracted zone where the test section is located and then passes through a diffuser, a fan section and an exhaust.

By the 1940’s supersonic wind tunnels were in use. In 1972, a cryogenic wind tunnel was built at NASA Langley by injecting liquid nitrogen into the wind tunnel to cool the gas. This lowered the viscosity and increased the Reynolds number, and this tunnel had the capability to match Reynolds and Mach numbers simultaneously up to Mach 1.2
\cite{fernandes_design_nodate}.

Today the largest wind tunnel in the world is the National Full-Scale Aerodynamics Complex at NASA's Ames Research Center, which has a test section of cross-section 80 ft by 100 ft (24 m x 31 m). The types of instruments in common use in wind tunnels include boundary layer rakes, tufts, pitot tubes, pressure sensitive paint, smoke, and static pressure taps \cite{morris_force_2010}.

NASA uses wind tunnels to test scale models of aircraft and spacecraft. The wind tunnels help to test ideas of making aeroplanes better and safer. They are also used to help engineers in designing spacecraft that will work in other planets such as mars - the wind tunnel can be used to simulate objects in an atmosphere that's thinner than ours e.g. an atmosphere that's exactly like the Martian atmosphere.
\begin{center}
	%&\vspace*{-4.0cm}
	\begin{figure}[H]
		\centering
		
		\caption[NASA Wind tunnel - space application]{NASA wind tunnels used to test the design of heavy-lift rocket \cite{NASA}}
	\end{figure}
\end{center}
NASA has wind tunnels of different types and sizes. Some are low-speed wind tunnels, others are hypersonic i.e. they are made to carry out tests at 4,000 mph (6437 kph) \cite{NASA}.
\subsection{Stewart Platform}
The Stewart platform is an example of a parallel manipulator.
Parallel link manipulators have become an important area of research due to their: precision, rigidity and high-load-to-weight ratio.
These manipulators find practical applications in flight simulators, precise machining and applications that require disturbance isolation \cite{iqbal_dynamic_2008}.

A Stewart platform is a parallel manipulator that provides six-degree-of-freedom (DOF) i.e. roll, pitch, yaw, surge, sway and heave (displacement in the z-direction), and can be controlled in all these freedoms simultaneously.
The platform consists six legs connecting a top plate to a base plate with spherical joints as the connection points.

The platform is able to move in three angular directions and in three linear directions, singly or in any combination \cite{stewart1965platform}. Angular and translational motion of the top plate with
respect to the base plate is achieved by reducing or extending the actuator lengths (for Stewart platforms with linear actuators for legs) or by writing various servo angles to the servo motors
(for Stewart platforms that use servo motors to actuate leg movements) \cite{iqbal_dynamic_2008}.

\subsubsection{Stewart Platform Configurations}
Stewart platforms can take three primary configurations i.e. 3-3 type, 3-6 type or 6-6 type.
\begin{center}
	\begin{figure}[H]
		\centering
		
		\caption[Configurations]{Type 3-3, 3-6 and 6-6 respectively
			\cite{fernandes_design_nodate}}
	\end{figure}
\end{center}
The base and the platform (for the 3-3 type), and the platform (for the 3-6 type) are triangular in shape. The triangular shape has a good load carrying capability only in theory and for certain dimensions. These configurations are, however,not possible in practice since double spherical joints will be needed where two bars have to be joined at the same vertex
\cite{fernandes_design_nodate}.

For a 6-6 type Stewart platform, the base and platform are hexagon in shape.

\subsection{Force Balances}
For wind tunnel applications, the wind axes is used as the reference frame. Where, X axis points to the accelerated air; Z axis points downward and; Y axis points to the right in the direction of the wind. In the reference frame above, lift is in the negative z-direction, drag in the negative x-direction and, side force in the negative y-direction \cite{bueno2018design}.

Moment components on the x,y,z axes are rolling moment, pitching moment and yawing moment respectively. A three-component force balance can be considered to measure the lift, drag and pitch (angle of attack).

Force balances can be external or internal. In external force balances the test section lies outside of the wind tunnel test section, whereas in internal force balances the balance is inside the model itself connecting the model to the support structure.
\subsubsection{External Force Balances}
Several different types of external force balances are available for wind tunnel use
\cite{morris_force_2010}:
\begin{enumerate}
	\item Wire
	\item Platform
	\item Yoke
	\item Pyramidal
\end{enumerate}
In the wire balance, the model under testing is suspended by wires each connected to an extensometer (a sensor that produces an electrical output when submitted to a load and deforms). The shortcoming of the wire balance is the large tare drag caused by the wires which is difficult to quantify. They are also not robust nor versatile enough compared with the other alternatives \cite{ferreira2015design}.
\begin{center}
	\begin{figure}[H]
		\centering
		
		\caption[Wire force balance]{Wire force balance \cite{ferreira2015design}}
	\end{figure}
\end{center}
The platform balance is relatively easy to construct, assemble and instrument. However, for this balance, forces and torques are coupled and the balance resolving center does not coincide with the center of the tunnel.
\begin{center}
	\begin{figure}[H]
		\centering
		
		\caption[Platform force balance]{Platform force balance \cite{ferreira2015design}}
	\end{figure}
\end{center}
In the yoke balance configuration, forces and torques are coupled and the balance resolving center coincides with the center of the tunnel. This configuration, however, presents some structural deflections due to the large span of the measuring and support arms.
\begin{center}
	\begin{figure}[H]
		\centering
		
		\caption[Yoke force balance]{Yoke force balance \cite{ferreira2015design}}
	\end{figure}
\end{center}
The pyramidal balance configuration is a further improvement of the yoke balance in order to overcome the shortcomings of the other balances. It is capable of measuring six components of forces and
torques separately and without coupling, provided that the balance is well assembled and calibrated.
\begin{center}
	\begin{figure}[H]
		\centering
		
		\caption[Pyramid force balance]{Pyramid force balance \cite{ferreira2015design}}
	\end{figure}
\end{center}
It is possible to merge some of the force balance concepts to come up with an innovative, easy-to-manufacture and cost-effective external force balance. One such solution can be the use of a Stewart platform as a force balance. The Stewart platform offers another advantage - dynamic positioning of the model in the test section.
The platform bars are subjected to axial forces only and can have strain-gages coupled to each one as Wheatstone bridges. Forces and torques are then obtained based on the axial displacements obtained by the strain gages\cite{fernandes_design_nodate}.

Table \ref{tablecom} shows a summary of advantages and disadvantages of external force balances.
\clearpage
\begin{center}
	\begin{table}[H]
		\caption[Comparison of Force Balances]{A Table of Comparison and Contrast of External Force Balances}
		\label{tablecom}
	
	\begin{tabular}{|l|l|l|}
		\hline
		\textbf{Type} & \textbf{Advantages}                         & \textbf{Disadvantages}        \\
		\hline
		Wire          & Relatively simple construction              & large tare drag               \\
		              &                                             & Less Versatile and robust     \\
		\hline
		Platform      & Easy construction and instrumentation        & Force and torques coupled     \\
		              &                                             & Center alignment difficulties \\
		\hline
		Yoke          & Overcomes center alignment problems         & Structural deflections        \\
		\hline
		Pyramidal     & Overcomes shortcoming of other balances     &                               \\
		              & Measures 6 components of forces and torques &                               \\
		\hline
	\end{tabular}
\end{table}
\end{center}
\subsubsection{Internal Force Balances}
The different kinds of internal balances can be made based on \cite{ferreira2015design}:
\begin{enumerate}
	\item The type of transducer i.e. strain gauge or piezoelectric balance.
	\item Shape i.e. box balance and sting balance
\end{enumerate}
\begin{center}
	\begin{figure}[H]
		\centering
		
		\caption[Internal force balances]{Typical configurations for internal force balances. \textit{Left to right:} Box balance and sting balance \cite{ferreira2015design}.}
	\end{figure}
\end{center}
The box balance presents a cubic shape and can either be made of a solid piece of material or from assembled parts. In this configuration, the loads are transferred from the top to the bottom. The sting balance presents a cylindrical shape and the loads are transferred from one end to the other in the longitudinal direction. It can be used to measure forces or torques.

The advantage of internal force balances is that they minimize the interference caused by the supporting bars in the flow.
\subsection{Sensors}
\subsubsection{Load Sensors}
Several methods can be used to measure forces and torques in a force balance. These methods can be generally grouped into two\cite{ferreira2015design}:
\begin{enumerate}
	\item Hydraulic measuring techniques.
	\item Electric measurement techniques.
\end{enumerate}
Electric measurement techniques are preferred for Force balance applications. One such electric measurement device is the strain gauge. A strain gauge is an electromechanical device whose electrical resistance changes linearly with the strain in the component.

Metal foil strain gauges are widely used. This type of strain gauges provide more precise strain values than wire strain gauges. However, since the relative changes on electric resistance of the strain gauge are so small, it is necessary to develop an effective method of measuring them because each strain gauge would require extremely accurate signal measurements. The solution is to have a set of strain gauges coupled in order to minimize the required accuracy, forming a force transducer i.e. the \textit{Wheatstone bridge}.
\begin{center}
	\begin{figure}[H]
		\centering
		
		\caption[Wheatstone Bridge Circuit]{Wheatstone Bridge Circuit \cite{ferreira2015design}}
	\end{figure}
\end{center}
Load cells can also be used to measure the drag and lift forces\cite{ferreira2015design}.
\subsubsection{Attitude Sensor}
It is important to define the desired aerodynamic angles and to guarantee that they are measured accurately in relation to the air stream. One such angle is the angle of attack (\textalpha) shown in Figure \ref{att}. For this reason, specific devices that provide the attitude measurement should be implemented in order to improve the precision of the results.

Angle of attack (\textalpha)is the angle measured between the longitudinal axis of the model and the direction of the flow on a vertical (Figure \ref{att})
\begin{center}
	\begin{figure}[H]
		\centering
		
		\caption[Angle of attack]{Angle of attack (\textalpha) \cite{ferreira2015design}}
		\label{att}
	\end{figure}
\end{center}

\subsection{Smoke visualization System for Wind Tunnel}
The ability to visualize the airflow over solid objects in a wind tunnel crucial in understanding the fundamental principles of both fluid dynamics and aerodynamics. To achieve this a uniform row of smoke lines are required. These smoke lines should be sufficiently long to maintain their integrity throughout
the test section \cite{trinder2013development}.

Smoke visualization methods including smoke-generating materials and techniques for generating smoke lines have been summarized in the tables below.
\begin{center}
	\begin{table}[H]
		\caption[Smoke Generating Materials]{Comparison of Smoke Generating Materials}
	
	\begin{tabular}{|p{5cm}|p{5cm}|p{5cm}|}
		\hline
		\textbf{Material}                            & \textbf{Advantages}                 & \textbf{Disadvantages}                                      \\
		\hline
		Tobacco, kerosene and titanium-tetrachloride & Produces high quality smoke         & Hazardous/toxic; tobacco is difficult to control           \\
		\hline
		Carbon dioxide                               & Produces dense smoke                & Potentially harmful in large volumes; needs to be exhausted \\
		\hline
		Water-based liquids                          & Non-hazardous; produce dense vapour & Vapour can condense back to liquid                          \\
		\hline
	\end{tabular}
\end{table}
\end{center}

\begin{center}
	\begin{table}[H]
		\caption[Smoke Generating Techniques]{Comparison of Smoke Generating Techniques}
	
	\begin{tabular}{|p{5cm}|p{5cm}|p{5cm}|}
		\hline
		\textbf{Technique} & \textbf{Advantages}                                & \textbf{Disadvantages}                      \\
		\hline
		Smoke wire         & Produces the most effective smoke lines            & Complex set-up to achieve resistive heating \\
		\hline
		Smoke rake         & Can be utilized with non-hazardous smoke materials & Prone to wind tunnel blockage effects       \\
		\hline
	\end{tabular}
\end{table}
\end{center}
For smoke rake, an aerodynamically shaped
body (typically elliptical) featuring a row of tubes through which the smoke exits is used. Smoke to the rake can be introduced from a non-hazardous source,
such as a water-based liquid heated by a
smoke machine, rather than using combustion of hydrocarbons as in the smoke wire technique, which is hazardous and produces toxic materials \cite{trinder2013development}.

\subsection{Previous Work}
Force balance design for educational wind tunnels is an area of great interest. This is especially important
for aerodynamics studies of aeroplanes and aerofoil models, as well as ground vehicles such as trucks
and cars \cite{morris_force_2010}.

Force balances can be used in conjunction with a linear actuator where the
actuator is mounted inside the force balance apparatus, using a parallel four-bar linkage so that
the angle of attack is linearly related to the actuator position. Alternatively, manipulators such as the Stewart platform can serve as force balances. This section presents some of the work that has been done in this area.
\subsubsection{Bradley University (USA)}
The Mechanical Engineering department of Bradley University has a force balance installed in the test-section of a subsonic wind tunnel. The force balance comprises of two load cells to measure lift and drag forces. A linear actuator is used in conjunction with the force balance to change the angle of attack of models during testing.
\begin{center}
	\begin{figure}[H]
		\centering
		
		\caption[Force balance installed]{Force balance installed in the wind tunnel \cite{morris_force_2010}}
	\end{figure}
\end{center}
There is a possibility of adding a third load cell to this configuration to enable measurement of the pitching moment. The force balance offers good results with lift and drag coefficients not changing by more than 10 percent with varying wind tunnel velocity in the range of Reynolds
numbers where the coefficients should be fairly constant \cite{morris_force_2010}.

The overall cost of coming up with this force balance is given as 1000 dollars which is significantly cheaper than the commercially available force balances. A two-component force balance goes for a minimum of 9385 dollars.
%\subsection{Inertial Measurement Units (IMUs)}
%IMU’s are sensors that combine an accelerometer, a gyroscope and, in other cases, a magnetometer.
%They're used widely due to their small size and low cost. The gyroscope measures the
%sensor’s angular velocity and the accelerometer is used to measure the external force acting on the
%sensor which is not only due to its acceleration but also to the gravity. The gyroscope measurements
%can provide the change in pitch, roll and yaw by integrating the values of angular velocities along the
%three axis, but to calculate absolute values of these angles, reference data is needed. This data can be
%obtained from the accelerometer or the magnetometer. It is possible to obtain pitch and roll angles from
%the accelerometer, putting  gravitational acceleration in consideration. However, yaw angle cannot
%be obtained directly from the results of the accelerometer as it is in the same direction as the gravity.
%For calculating yaw, the data from the magnetometer as reference and then integrates the gyroscope
%information \cite{ferreira2015design}.
%\begin{center}
%	\begin{figure}[H]
%\centering
%\includegraphics[width=0.6\linewidth]{Figures/imu}
%\caption[Inertial Measurement Unit]{IMU (MPU 6050) \cite{ferreira2015design}}
%\end{figure}
%\end{center}
\subsubsection{East Africa School of Aviation (EASA)}
The EASA Aerodynamics lab has a subsonic wind tunnel 300mm (AF1300) and a flight demonstration wind tunnel(AF41) supplied by TECQUIPMENT. The Subsonic wind tunnel is equipped with a three-component force balance, smoke generator, multi-tube manometer and a range of aerofoil drag, boundary layer low and high wing models. The Flight demonstration wind tunnel has a data acquisition module for classroom demonstrations and investigations into the behaviour of fixed-wing aircraft and wing-performance during take-off, flight and landing \cite{TEC}.

\subsubsection{Tecnico Lisboa}
In 2018, Joao Fernandes of Tecnico Lisboa developed a force balance system to
be used with the aerospace engineering laboratory wind tunnel. The project was to
design a force balance measuring the six components. A Stewart platform was used as the
force and measurement system which was made possible through instrumentation of the platform legs.
For sensing, strain gauges were used and connected in a Wheatstone bridge configuration.
The system was able to measure all the six components of aerodynamic properties\cite{ferreira2015design}.

Further developments were made two years later to this design which are enumerated below \cite{ferreira2015design}:
\begin{enumerate}
	\item The use of a half bridge configuration of strain gauge for the measurement system.
	\item Use of an Arduino DAQ system for temperature and humidity monitoring to help in
	      compensation of switching to a half bridge configuration for the strain gauges.
\end{enumerate}
\subsubsection{Stewart Platform at JKUAT}
Six-DOF Stewart platforms have been designed and fabricated by students in the Mechatronic Engineering department as part of their final year projects. The Stewart platforms by the first two groups of students were for different applications and the one from FYP-17 was to be used as a force balance for Wind tunnel testing \cite{caleb}. Although the Stewart platform was built successfully, the group didn't achieve a force balance for the same.
\subsection{Summary of Gaps}
Whereas the Force balance by the Mechanical Engineering department in Bradley University is relatively simple to construct, it still poses a challenge in terms of cost. Cost can be minimized based on load cell and actuator selection but this does not guarantee that the level of accuracy will not be compromised. Also, only two or three force components can be obtained. The force balance setup doesn't allow dynamic positioning of models in the wind tunnel during testing.

Institutions such as EASA have procured their force balances. The force balances guarantee high accuracy but this may not be a cost-effective solution.

With so much research in the area of Stewart platform, there remains still more work to be done in the areas of control, dynamics, and singular positions.The Stewart platform force balance by Joao,for example, doesn't have actuation \cite{ferreira2015design}.

A 6 DOF Stewart platform with force measurement for a low-speed wind tunnel has been done as final year project in JKUAT under the department of Mechatronic Engineering (FYP 17). Whereas the former team was able to successfully design and assemble the platform, as well as the actuation circuitry, there still remains work to do in the following areas \cite{caleb}:
\begin{enumerate}
	\item Development of a Human-Machine-Interface for Stewart platform control.
	\item Data acquisition from sensors.
	\item Implementation of servo circuit control.
	\item Calibration of the measurement system to be in-line with NASA aerofoils.
\end{enumerate}

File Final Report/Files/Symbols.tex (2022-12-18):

\section*{List of Symbols}
    $B_{k}$ - leg attachment on base\\
    $H_{k}$ - Servo horn anchor\\
    $\vec{b}_i$ - position of ith connection point at base with respect to B\\
    $\vec{F}_e$ - external force applied to platform\\
    $f_i$ - force exerted on ith leg due $F_e, M_e$\\
    $F$ - vector of leg forces\\
    $\hat{I}_i$ - Unit vector along the ith leg\\
    $\vec{M}_e$ - external moment applied to platform\\
    $\hat{{S_{i}}}$ - unit vector of the Plucker coordinates\\
    $\alpha$ - Angle of attack\\
    $\alpha_{k}$ - Servo angle\\
    $\beta$ - Side slip angle\\
    $\beta_{k}$ - servo rotation angle form plan view\\
    $\epsilon$ - Strain\\
    $|h|$ - distance between original base anchor and platform anchor\\
    $|J|$ - determinant of Jacobian matrix\\
    $|J|_{m}$ - determinant of Jacobian matrix of optimal Stewart Platform configuration\\
    $\lambda$ - Quality index\\
    $l_{k}$ - leg length\\
    $P_{k}$ - leg attachment on platform\\
    $^{p}R_{b}$ - Rotation of the platform\\
    $R_{y}$ - rotation about y-axis\\
    $R_{z}$ - rotation about z-axis\\
    $\sigma$ - Stress\\
    $^{p}T_{b}$ - translation from the base origin to the platform origin\\
    $t_{x}$ -  translation in the x direction\\
    $t_{y}$ -  translation in the y direction\\
    $t_{z} $ -  translations in the z direction\\
\pagebreak

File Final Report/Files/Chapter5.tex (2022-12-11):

\section{Conclusion}
The current Stewart platform configuration was modified to allow for six degrees of freedom which includes three translations and three rotations.
From Finite Element Analysis, the six legs of the Stewart platform experience significant strains which can be used to obtain force measurements during model testing in wind tunnel experiments.
The electronic circuit to obtain flow velocity measurements and load measurements was also demonstrated. This also included the sensor selection and placement in the wind tunnel.
The Human machine interactive interface was also developed and tested.
The force balance was tested utilizing a real aerofoil model and the system was shown to be working as per specifications.

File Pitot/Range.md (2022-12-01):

# Pressure Ranges at various speeds
11020pa - 11251pa at 30m/s

11509pa - 11904pa at 40m/s

11966pa - 12326pa at 50m/s

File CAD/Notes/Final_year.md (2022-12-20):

# Final Year Report
## Outline 
0. ~~ Title page ~~
1. Abstract
2. Introduction (Chapter 1)
3. Literature Review (Chapter 2)
4. Methodology (Chapter 3)
5. Results and Discussion (Chapter 4)
6. Conclusion (Chapter 5)

**Problem Statement**

We need A STATEMENT for our problem STATEMENT

The force balances used in wind tunnel testing have to incorporate linear actuators in order to alter model position. This, however, only changes the model's angle of attack and dynamic orientation of models is impossible to achieve. 

Line 44 to talk about servos actuating the Stewart platform movements

**Smoke Visualization Technique for Wind Tunnel**

The ability to visualise the airflow over solid objects in a wind tunnel crucial in understanding the fundamental principles of both fluid dynamics and aerodynamics. To achieve this a uniform row of smoke lines are required. These smoke lines should be sufficiently long to maintain their integrity throughout the test section.

Smoke visualization methods including smoke-generating materials and techniques for generating smoke lines have been summarized in the tables below.

The application smoke lines over several test objects, such as wing sections and bluff body shapes, ensures high-quality visualisations.

Carbon dioxide
Produces dense smoke
Potentially harmful in large volumes;
Non-hazardous; produce dense vapour
Vapour can condense back to liquid

Smoke wire
Produces the most effective smoke lines
Can be utilised with non-hazardous smoke materials

For smoke rake, an aerodynamically shaped
body (typically elliptical) featuring a row of tubes through which the smoke exits is used. Smoke to the rake can be introduced from a non-hazardous source, such as a water-based liquid heated by a smoke machine, rather than using combustion of hydrocarbons as in the smoke wire technique, which is hazardous and produces toxic materials.

## Methodology

### Instrumentation of the Stewart Platform

From FEA done on the Stewart platform, strain values were expected along the Stewart platform legs as shown in figure \ref{eq}.

## Electromechanical Modifications

To implement streamline smoke lines in the wind tunnel, a smoke rake, which is an aerodynamically shaped
body (typically elliptical) featuring a row of tubes through which the smoke exits was designed. The CAD model was deigned using Autodesk Inventor and the rake was prepared for 3D printing at iPIC in JKUAT. The rake design is shown below.

To implement smoke visualisation in the wind tunnel, the rake is used in conjuction with:

## Smoke rake
Change top hole diameter to 20mm

## CFD Parameters
1. Simulation - Fluid Flow Fluent
2. Simulation type - steady flow
3. Diameter of strut - 12.5mm
4. Area - 
5. Mesh size - 0.001mm
6. Growth rate - default (1.2)
7. Behavior - soft
8. Defeature size - 5.5902 e-004m

## Specific Objectives
To develop a force balance for the Stewart platform and obtain forces and moments
measurement during model testing.

To obtain flow velocity measurement in the wind tunnel by use of pitot tubes.

To develop a Human-Machine Interface for measurement readings and control of
the Stewart platform load balance.

To improve model behaviour visualization in the wind tunnel by introduction of
smoke streamlines in the wind tunnel

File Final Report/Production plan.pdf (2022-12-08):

Production plan - Final Year projects 2022
Title: Development of a 6 DOF Stewart Platform Force Balance for a Low Speed Wind Tunnel
Week | Tasks/Activities | Materials Required | Special Equipment | Simulteneous/Concurrent activities | Status/remarks
1 | 1. Order of PCBs from China and HX711s locally. 2. Project presentation. | NONE | NONE | Assembly of Stewart platform.
| 2. Project presentation | NONE | NONE
2 | 1. Program the Human Machine Interface | NONE | NONE | Design of streamline smoke visualizer
| 2. Location of drilling points on the wind tunnel for three pitot tubes (i) Determining hole positions in the intake and diffuser sections. (ii) Determining distance between holes in intake and diffuser sections (iii) Determing hole dimension based on pitot tube diameter | NONE | NONE
3 | 1. Test and calibrate the three pitot tubes. (i) Obtain readings from each pitot tube separately. (ii) Test all three pitot tubes in the same conditions and ensure we get similar results | NONE | NONE | Verify and 3D print streamline smoke emitter
| 2. Control Stewart platform using HMI (i) Achieve different Stewart platform movements based on HMI commands | NONE | NONE


Production plan - Final Year projects 2022
Title: Development of a 6 DOF Stewart Platform Force Balance for a Low Speed Wind Tunnel

Week | Tasks/Activities | Materials Required | Special Equipment | Simulteneous/Concurrent activities | Status/remarks

4 | 1. Drill holes on the wind tunnel for mountin the pitot tubes. (i) Drill dia 7mm holes in the intake and diffuser sections of the wind tunnel | Rubber | 1. Hand drill. Specific drill bit diameter i.e. 7mm | Circuit Assembly.

5 | 1. Assembly of smoke visualizer in the Wind Tunnel (i) Design assembly setup of the smoke visualizer in the wind tunnel (ii) Pipe threading to support smoke visualizer in wind tunnel (iii) Drill hole on the wind tunnel to allow introduction of smoke into the wind tunnel | 3/4" metal pipe (galvanized/black). 400mm length | Pipe wrench Hand drill Drill bit (diameter 20mm) | Attach strain gauges on one Stewarat platform leg as a demo

6 | Attach strain gauges on Stewart platform legs. | | NONE

7 | 1. Full assembly. (i) Control Stewart platform using HMI (ii) Obtain force and pressure readings. | NONE | NONE | Sample model testing

2. Assembly of smoke visualizer and pitot tubes in the wind tunnels (i) Install smoke visualizer in the wind tunnel and connect to the fog generator | | | Sample model testing

8 | Iterative testing."1. Obtain pressure readings (i) Display pressure readings on HMI | NONE | NONE | Calibrate platform

Production plan - Final Year projects 2022
Title: Development of a 6 DOF Stewart Platform Force Balance for a Low Speed Wind Tunnel
Week | Tasks/Activities | Materials Required | Special Equipment | Simulteneous/Concurrent activities | Status/remarks
| 2. Force sensor testing (i) Obtain forces and moments form the Stewart platform force balance (ii) Display force measurements on HMI | Adherant
9 | Iterative testing. | NONE | NONE
10 | Iterative testing. | NONE | NONE
11 | Iterative testing. | NONE | NONE
12 | Iterative testing. | NONE | NONE
13 | Iterative testing. | NONE | NONE
14 | Iterative testing. | NONE | NONE

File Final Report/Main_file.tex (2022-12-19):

\documentclass[12pt,fleqn]{article}
\usepackage{a4}
\usepackage{graphicx}
\usepackage{psfrag}
\usepackage{amsmath}                     % \boldsymbol{#1}
\usepackage{amssymb}

%\usepackage{hangcaption}
%\usepackage{Styles/pstricks}
%\usepackage{Styles/pst-node}
\usepackage{Styles/fancyheadings}
\usepackage{tocloft}
\usepackage[euler]{textgreek}
\usepackage{booktabs}
\usepackage{mhchem}
\usepackage{siunitx}
\usepackage{bm}
\usepackage{tabularx,ragged2e,rotating}
\newcolumntype{C}{>{\hspace{0pt}%
    \Centering\arraybackslash}X}
\usepackage[skip=0.333\baselineskip]{caption}
\usepackage{longtable}
\usepackage{pdflscape}
\usepackage{subfig}
\usepackage{psfrag}
%\usepackage{mathtools}
%\usepackage{unicode-math}
%\setmathfont{XITS Math}
%\newcommand*{\matr}[1]{\mathbfit{#1}}
%\newcommand*{\tran}{^\mkern-1.5mu\mathsf{T}}}
%\newcommand*{\conj}[1]{\overline{#1}}
%\newcommand*{\hermconj}{^{mathsf{H}}}
\usepackage{MnSymbol}
\usepackage{pdfpages}
%\usepackage{breqn}
\usepackage{float}
\usepackage{nccmath}
%\usepackage{chngcntr}
%-----Tex width---------------------------------
\textwidth 16cm

%\counterwithout{figure}{chapter}

%-----Line spacing-------------------------------
\renewcommand{\baselinestretch}{1.5}     % 1,1-zeilig

%---------Add dots in TOC-----------------------
\renewcommand{\cftsecleader}{\cftdotfill{\cftdotsep}}

%------Paragraph indention-------------------------------
\setlength{\parskip}{1.5ex plus0.5ex minus0.5ex}

%-----Prevent indent----------------------
\setlength{\parindent}{0em}

%-----Richtiger Abstand fur Einheiten-------------
\def\Unit{\hspace{0.25em}}

%-----Definition of the header--------------------
\pagestyle{fancyplain}
\renewcommand{\sectionmark}[1]{\markboth{Chapter~\thesection.~#1}{#1}}
\renewcommand{\subsectionmark}[1]{\markright{\thesubsection\ #1}}
\rhead[\fancyplain{}{\leftmark}]%
{\fancyplain{\thepage}{\thepage}} \cfoot{} \plainheadrulewidth
0.4pt
%% Otherwise: Overfull \vbox-Warning against fancyheadings-pacakage
%%  idea of: nic@minster.york.ac.uk (Nick Cropper)
\makeatletter
\ifcase \@ptsize \relax % 10pt
  \addtolength{\headheight}{1\p@}
\or % 11pt
  \addtolength{\headheight}{2\p@}
\or % 12pt
  \addtolength{\headheight}{3\p@}
\fi \makeatother

%-----Equations / Figures / Tables numbering according to \ sections
\makeatletter
\renewcommand\theequation{\arabic{section}.\arabic{equation}}
\renewcommand\thefigure{\arabic{section}.\arabic{figure}}
\renewcommand\thetable{\arabic{section}.\arabic{table}}
\@addtoreset{equation}{section} \@addtoreset{figure}{section}
\@addtoreset{table}{section} \makeatother

%-----Useful abbreviations----------------------
\newcommand{\mr}{\mathrm}
%%\newcommand{\bs}[1]{\mbox{$\boldsymbol{#1}$}}
\newcommand{\degree}[1]{\mbox{$#1^\circ$}}

%\renewcommand{\figurename}{Bild}

%------Bibliography style-----------------------
\bibliographystyle{IEEEtran}

%-----Aufzaehlunstiefe im Literaturverzeichnis---------------
\setcounter{tocdepth}{3}

\begin{document}
\pagenumbering{Roman}
\begin{titlepage}
  \begin{center}
    \vspace*{-4.0cm}
    \begin{figure}[!h]
      \centering
      
      %\caption{}
      \label{fig:jomologo}
    \end{figure}
    \large{Jomo Kenyatta University of Agriculture and Technology}\\
    \large{College of Engineering and Technology}\\
    \large{School of Mechanical, Materials, and Manufacturing Engineering}\\
    \large{Department of Mechatronic Engineering}\\

    ------------------------------------------------------------------------------------------------\\[0.1cm]
    \vspace{0.1cm}
    \LARGE{\textbf{Development of a 6 DOF Stewart platform
        Force Balance for a Low Speed Wind Tunnel}}\\
    \vspace{0.2cm}
    \LARGE{\large\textbf{FYP 18-9
      }}\\
    {\large\textbf{FINAL PROJECT REPORT
    }}\\[0.1cm]
    %\large{by}\\[0.6cm

    \vspace{0.1cm}
    \large{\textbf{Sammy Kerata Oina (ENM221-0089/2017)
      }}\\
    \large{\textbf{Earl Spencer Mogire~(ENM221-0074/2017)
      }}\\[0.3cm]
    \large{\textbf{Supervisors}}\\
    \large{Dr. Anthony K. Muchiri
    }\\
    %\large{Ms. Maurine N. Andanje
    %}\\
    \large{\textbf{Technologist}}\\
    \large{Mr. J Mbugua
    }\\
    %Submitted in partial fulfilment of the requirements for the degree of Bachelor of Science in Mechatronic Engineering in Jomo Kenyatta University of Agriculture and Technology, 2022.
    %     \large{\textbf{Supervisors}}\\
    %    \large{Dr.-Ing.~Jackson G. Njiri}\\
    %    \large{Prof. George N. Nyakoe}\\
    %    \large{\ldots}    \\[0.2cm]\vfill
    \large{\small{\today}}\\
    \small{Submitted in partial fulfillment of the requirements for the degree of Bachelor of Science in Mechatronic Engineering in Jomo Kenyatta University of Agriculture and Technology, 2022.}
    ------------------------------------------------------------------------------------------------\\[1.5cm]
  \end{center}
\end{titlepage}
%
%\pagenumbering{gobble}% Remove page numbers (and reset to 1)

\input{Files/Declaration}
\clearpage
\input{Files/Abstract}
\clearpage
\input{Files/Acknowledgment}
\clearpage
\addcontentsline{toc}{section}{Table of Contents}
\tableofcontents
\clearpage
\addcontentsline{toc}{section}{List of Figures}
{
%
\let\oldnumberline\numberline%
\renewcommand{\numberline}{\figurename~\oldnumberline}%
\listoffigures
\clearpage
\addcontentsline{toc}{section}{List of Tables}
\renewcommand{\numberline}{\tablename~\oldnumberline}%
\listoftables
\newpage
\clearpage
%\addcontentsline{toc}{section}{List of Abbreviations}
\input{Files/Nomenclature}
\clearpage
\newpage
%\addcontentsline{toc}{section}{List of Symbols}
\input{Files/Symbols}
\clearpage
\newpage

\newpage
\pagenumbering{arabic}
\input{Files/Introduction}
\clearpage
\input{Files/Chapter2}
\clearpage
\input{Files/Chapter3}
\clearpage
\input{Files/Chapter4}
\clearpage
\input{Files/Chapter5}
%  \clearpage
%\input{Files/Summary}
\clearpage
%----  Bibliography  ----------------------------------------
\markright{References}                               % Erzeugt Kopfzeile
\addcontentsline{toc}{section}{References}            % Literaturverzeichnis ins Inhaltsverzeichnis
%\bibliographystyle{Bib/IEEEtran}
\bibliography{Bib/References}                         % BIBTeX
\nocite{Lun01}

% Falls etwas in die Literaturliste soll, was nicht Referenziert wird
\newpage
\clearpage
\input{Files/Appendices}
\end{document}

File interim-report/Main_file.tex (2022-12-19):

\documentclass[12pt,fleqn]{article}
\usepackage{a4}
\usepackage{graphicx}
\usepackage{psfrag}
\usepackage{amsmath}                     % \boldsymbol{#1}
\usepackage{amssymb}

%\usepackage{hangcaption}
%\usepackage{Styles/pstricks}
%\usepackage{Styles/pst-node}
\usepackage{Styles/fancyheadings}
\usepackage{tocloft}
\usepackage[euler]{textgreek}
%\usepackage{mathtools}
%\usepackage{unicode-math}
%\setmathfont{XITS Math}
%\newcommand*{\matr}[1]{\mathbfit{#1}}
%\newcommand*{\tran}{^\mkern-1.5mu\mathsf{T}}}
%\newcommand*{\conj}[1]{\overline{#1}}
%\newcommand*{\hermconj}{^{mathsf{H}}}
\usepackage{MnSymbol}
\usepackage{pdfpages}
%\usepackage{breqn}
\usepackage{float}
\usepackage{nccmath}
%\usepackage{chngcntr}
%-----Tex width---------------------------------
\textwidth 16cm

%\counterwithout{figure}{chapter}

%-----Line spacing-------------------------------
\renewcommand{\baselinestretch}{1.5}     % 1,1-zeilig

%---------Add dots in TOC-----------------------
\renewcommand{\cftsecleader}{\cftdotfill{\cftdotsep}}

%------Paragraph indention-------------------------------
\setlength{\parskip}{1.5ex plus0.5ex minus0.5ex}

%-----Prevent indent----------------------
\setlength{\parindent}{0em}

%-----Richtiger Abstand fur Einheiten-------------
\def\Unit{\hspace{0.25em}}

%-----Definition of the header--------------------
\pagestyle{fancyplain}
\renewcommand{\sectionmark}[1]{\markboth{Chapter~\thesection.~#1}{#1}}
\renewcommand{\subsectionmark}[1]{\markright{\thesubsection\ #1}}
\rhead[\fancyplain{}{\leftmark}]%
{\fancyplain{\thepage}{\thepage}} \cfoot{} \plainheadrulewidth
0.4pt
%% Otherwise: Overfull \vbox-Warning against fancyheadings-pacakage
%%  idea of: nic@minster.york.ac.uk (Nick Cropper)
\makeatletter
\ifcase \@ptsize \relax % 10pt
  \addtolength{\headheight}{1\p@}
\or % 11pt
  \addtolength{\headheight}{2\p@}
\or % 12pt
  \addtolength{\headheight}{3\p@}
\fi \makeatother

%-----Equations / Figures / Tables numbering according to \ sections
\makeatletter
\renewcommand\theequation{\arabic{section}.\arabic{equation}}
\renewcommand\thefigure{\arabic{section}.\arabic{figure}}
\renewcommand\thetable{\arabic{section}.\arabic{table}}
\@addtoreset{equation}{section} \@addtoreset{figure}{section}
\@addtoreset{table}{section} \makeatother

%-----Useful abbreviations----------------------
\newcommand{\mr}{\mathrm}
%%\newcommand{\bs}[1]{\mbox{$\boldsymbol{#1}$}}
\newcommand{\degree}[1]{\mbox{$#1^\circ$}}

%\renewcommand{\figurename}{Bild}

%------Bibliography style-----------------------
\bibliographystyle{IEEEtran}

%-----Aufzaehlunstiefe im Literaturverzeichnis---------------
\setcounter{tocdepth}{3}

\begin{document}
\pagenumbering{Roman}
\begin{titlepage}
  \begin{center}
      \vspace*{-4.0cm}
    \begin{figure}[!h]
\centering

%\caption{}
\label{fig:jomologo}
\end{figure}
   \large{Jomo Kenyatta University of Agriculture and Technology}\\
    \large{College of Engineering and Technology}\\
    \large{School of Mechanical, Materials, and Manufacturing Engineering}\\
   \large{Department of Mechatronic Engineering}\\

    ------------------------------------------------------------------------------------------------\\[1.0cm]
    \vspace{0.1cm}
    \LARGE{\textbf{Development of a 6 DOF Stewart platform
        Force Balance for a Low Speed Wind Tunnel}}\\
    \vspace{0.3cm}
    \LARGE{\textbf{FYP 18-9
            }}\\
    {\textbf{INTERIM REPORT
                }}\\[0.4cm]
    %\large{by}\\[0.6cm

    \vspace{0.4cm}
    \large{\textbf{Sammy Kerata Oina (ENM221-0089/2017)
            }}\\
     \large{\textbf{Earl Spencer Mogire~(ENM221-0074/2017)
            }}\\[0.6cm]
    \large{\textbf{Supervisors}}\\
    \large{Dr. Anthony K. Muchiri
                }\\
    \large{Ms. Maurine N. Andanje
                    }\\
     %Submitted in partial fulfillment of the requirements for the degree of Bachelor of Science in Mechatronic Engineering in Jomo Kenyatta University of Agriculture and Technology, 2022.
%     \large{\textbf{Supervisors}}\\
%    \large{Dr.-Ing.~Jackson G. Njiri}\\
%    \large{Prof. George N. Nyakoe}\\
%    \large{\ldots}    \\[0.2cm]\vfill
    \large{\small{\today}}\\
    \small{Submitted in partial fulfillment of the requirements for the degree of Bachelor of Science in Mechatronic Engineering in Jomo Kenyatta University of Agriculture and Technology, 2022.}
    ------------------------------------------------------------------------------------------------\\[1.5cm]
  \end{center}
\end{titlepage}
%
%\pagenumbering{gobble}% Remove page numbers (and reset to 1)

\input{Files/Declaration}
\clearpage
\input{Files/Abstract}
\clearpage
\input{Files/Acknowledgment}
\clearpage
\addcontentsline{toc}{section}{Table of Contents}
\tableofcontents
\clearpage
\addcontentsline{toc}{section}{List of Figures}
{
%
\let\oldnumberline\numberline%
\renewcommand{\numberline}{\figurename~\oldnumberline}%
\listoffigures
\clearpage
\addcontentsline{toc}{section}{List of Tables}
\renewcommand{\numberline}{\tablename~\oldnumberline}%
\listoftables 
\newpage
\clearpage
%\addcontentsline{toc}{section}{List of Abbreviations}
\input{Files/Nomenclature}
\clearpage
\newpage
%\addcontentsline{toc}{section}{List of Symbols}
\input{Files/Symbols}
\clearpage
\newpage

\newpage
\pagenumbering{arabic}
  \input{Files/Introduction}
  \clearpage
  \input{Files/Chapter2}
  \clearpage
    \input{Files/Chapter3}
  \clearpage
    \input{Files/Chapter4}
  \clearpage
    \input{Files/Chapter5}
%  \clearpage
 %\input{Files/Summary}
  \clearpage
%----  Bibliography  ----------------------------------------
\markright{References}                               % Erzeugt Kopfzeile
\addcontentsline{toc}{section}{References}            % Literaturverzeichnis ins Inhaltsverzeichnis
%\bibliographystyle{Bib/IEEEtran}
\bibliography{Bib/References}                         % BIBTeX
\nocite{Lun01} 

                                     % Falls etwas in die Literaturliste soll, was nicht Referenziert wird
\newpage
\clearpage
\input{Files/Appendices}
\end{document}

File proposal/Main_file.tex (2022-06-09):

\documentclass[12pt,fleqn]{article}
\usepackage{a4}
\usepackage{graphicx}
\usepackage{psfrag}
\usepackage{amsmath}                     % \boldsymbol{#1}
\usepackage{amssymb}
%\usepackage{hangcaption}
%\usepackage{Styles/pstricks}
%\usepackage{Styles/pst-node}
\usepackage{Styles/fancyheadings}
\usepackage{tocloft}
\usepackage[euler]{textgreek}
%\usepackage{mathtools}
%\usepackage{unicode-math}
%\setmathfont{XITS Math}
%\newcommand*{\matr}[1]{\mathbfit{#1}}
%\newcommand*{\tran}{^\mkern-1.5mu\mathsf{T}}}
%\newcommand*{\conj}[1]{\overline{#1}}
%\newcommand*{\hermconj}{^{mathsf{H}}}
\usepackage{MnSymbol}
%\usepackage{breqn}
%-----Tex width---------------------------------
\textwidth 16cm

%-----Line spacing-------------------------------
\renewcommand{\baselinestretch}{1.5}     % 1,1-zeilig

%---------Add dots in TOC-----------------------
\renewcommand{\cftsecleader}{\cftdotfill{\cftdotsep}}

%------Paragraph indention-------------------------------
\setlength{\parskip}{1.5ex plus0.5ex minus0.5ex}

%-----Prevent indent----------------------
\setlength{\parindent}{0em}

%-----Richtiger Abstand fur Einheiten-------------
\def\Unit{\hspace{0.25em}}

%-----Definition of the header--------------------
\pagestyle{fancyplain}
\renewcommand{\sectionmark}[1]{\markboth{Chapter~\thesection.~#1}{#1}}
\renewcommand{\subsectionmark}[1]{\markright{\thesubsection\ #1}}
\rhead[\fancyplain{}{\leftmark}]%
{\fancyplain{\thepage}{\thepage}} \cfoot{} \plainheadrulewidth
0.4pt
%% Otherwise: Overfull \vbox-Warning against fancyheadings-pacakage
%%  idea of: nic@minster.york.ac.uk (Nick Cropper)
\makeatletter
\ifcase \@ptsize \relax % 10pt
  \addtolength{\headheight}{1\p@}
\or % 11pt
  \addtolength{\headheight}{2\p@}
\or % 12pt
  \addtolength{\headheight}{3\p@}
\fi \makeatother

%-----Equations / Figures / Tables numbering according to \ sections
\makeatletter
\renewcommand\theequation{\thesection.\arabic{equation}}
\renewcommand\thefigure{\thesection.\arabic{figure}}
\renewcommand\thetable{\thesection.\arabic{table}}
\@addtoreset{equation}{section} \@addtoreset{figure}{section}
\@addtoreset{table}{section} \makeatother

%-----Useful abbreviations----------------------
\newcommand{\mr}{\mathrm}
%%\newcommand{\bs}[1]{\mbox{$\boldsymbol{#1}$}}
\newcommand{\degree}[1]{\mbox{$#1^\circ$}}

%\renewcommand{\figurename}{Bild}

%------Bibliography style-----------------------
\bibliographystyle{IEEEtran}

%-----Aufzaehlunstiefe im Literaturverzeichnis---------------
\setcounter{tocdepth}{3}

\begin{document}
\pagenumbering{Roman}
\begin{titlepage}
  \begin{center}
      \vspace*{-4.0cm}
    \begin{figure}[!h]
\centering

%\caption{}
\label{fig:jomologo}
\end{figure}
   \large{Jomo Kenyatta University of Agriculture and Technology}\\
    \large{College of Engineering and Technology}\\
    \large{School of Mechanical, Materials, and Manufacturing Engineering}\\
   \large{Department of Mechatronic Engineering}\\

    ------------------------------------------------------------------------------------------------\\[1.0cm]
    \LARGE{\textbf{Development of a 6 DOF Stewart platform
        Force Balance for a Low Speed Wind Tunnel}}\\[0.6cm]
    \LARGE{\textbf{Final year proposal (FYP 18-9)
            }}\\[1.5cm]
    %\large{by}\\[0.6cm

    \vspace{0.5cm}
    \large{\textbf{Sammy Kerata Oina (ENM221-0089/2017)
            }}\\
     \large{\textbf{Earl Spencer Mogire~(ENM221-0074/2017)
            }}\\[1.0cm]
%     \large{\textbf{Supervisors}}\\
%    \large{Dr.-Ing.~Jackson G. Njiri}\\
%    \large{Prof. George N. Nyakoe}\\
%    \large{\ldots}    \\[0.2cm]\vfill
    \large{\small{\today}}\\
    ------------------------------------------------------------------------------------------------\\[1.5cm]
  \end{center}
\end{titlepage}
%
%\pagenumbering{gobble}% Remove page numbers (and reset to 1)

\input{Files/Declaration}
\clearpage
\addcontentsline{toc}{section}{Table of Contents}
\tableofcontents
\clearpage
\addcontentsline{toc}{section}{List of Figures}
{
%
\let\oldnumberline\numberline%
\renewcommand{\numberline}{\figurename~\oldnumberline}%
\listoffigures
\clearpage
\addcontentsline{toc}{section}{List of Tables}
\renewcommand{\numberline}{\tablename~\oldnumberline}%
\listoftables 
\newpage
\clearpage
\addcontentsline{toc}{section}{List of Abbreviations}
\clearpage
\newpage

\newpage
\input{Files/Abstract}
\clearpage
\pagenumbering{arabic}
  \input{Files/Introduction}
  \clearpage
  \input{Files/Chapter2}
  \clearpage
    \input{Files/Chapter3}
  \clearpage
    \input{Files/Chapter4}
%  \clearpage
%  \input{Files/Summary}
  \clearpage
%----  Bibliography  ----------------------------------------
\markright{References}                               % Erzeugt Kopfzeile
\addcontentsline{toc}{section}{References}            % Literaturverzeichnis ins Inhaltsverzeichnis
\bibliographystyle{Bib/IEEEtran}
\bibliography{Bib/References}                         % BIBTeX
\nocite{Lun01} 

                                     % Falls etwas in die Literaturliste soll, was nicht Referenziert wird
\end{document}

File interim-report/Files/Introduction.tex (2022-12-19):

\section{Introduction}
\label{sec:introduction}
Obtaining and simulating the aerodynamic performance of items in a wind tunnel is a
significant and important part in the development of vehicles, aircraft and other machines
that require aerodynamic performance evaluation. Due to the complex maneuvers that
may require simulation, there is a need for dynamic positioning of the model of the object
in the wind tunnel.
\subsection{Background}
A Stewart platform is a six degree-of-freedom mechanism that consists of a base and a platform connected with six legs that can vary in length. Each leg of the Stewart platform is connected to the ground by a two-axis joint and is provided with controllable means for extending its length
\cite{wittenburg2016stewart}. The six DOF Stewart Platform provides an elegant design for simulating flight conditions.\cite{stewart1965platform}. 

The Stewart platform can be used in conjunction with wind tunnels for wind tunnel testing. Wind tunnels are used to measure the aerodynamic forces on airplanes, wings, cars, trucks, bridges, and buildings. This can be done by positioning models of these vehicles in the tunnel's test section. The Stewart platform can provide various dynamic positions to simulate complex vehicle maneuvers. A force balance is incorporated to take direct measurement of forces and torques acting on the model that is being tested in the wind tunnel.

For this project, the force balance is intended to be built as simple and accessible as possible. Thus, use of a six DOF Stewart Platform as a force balance. A Stewart Platform has already been designed and fabricated by a previous group but is not integrated with a force balance. Electrical load measurement devices have to be connected to the legs of the Stewart platform in order to measure and obtain the results and so making it fully operational.

\subsection{Problem Environment}
Simulation and analysis of scaled models is an important step in the development of aircraft, vehicles and other machines. Such analysis provides aerodynamic performance data that can be used to inform any modifications or improvements e.g. in aircraft and vehicles to make them more efficient and safer. One such method that is used to perform aerodynamic performance evaluation is the wind tunnel used in conjunction with sensors for data acquisition by a computer. External or internal six-component force balances are also used. Another such technology that can be used for this purpose is the Stewart platform, which can be used to predict behaviour of vehicles and aircraft in the actual environment.

Whereas the force balances give very accurate results, some are expensive to build and use. Also, some objects require complex maneuver simulations to imitate the actual movements in air. There is therefore the need for dynamic positioning of objects in the wind tunnel.
\subsection{Problem Statement}
Measured parameter obtained in aerodynamic testing are critical in development of parts. Current commercial force balances provide means to position models and obtained forces and moments during testing. 
However, these force balances are quite expensive and some do not provide an integrated solution. This project goes through the development of a stewart platform force balance which aims to provide a cost effective solution for the low speed wind tunnel available at the Engineering fluids lab at JKUAT. 
The stewart platform force balance is meant to be able to measure 6 component aerodynamic loads as well as position the model within the wind tunnel with six degrees of freedom.
\subsection{Objectives}
\subsubsection{Main Objective}
\paragraph{} To develop a force balance and a control system for the Stewart platform. 
\subsubsection{Specific Objectives}
\begin{enumerate}
\item To evaluate the mechanical feasibility of the already fabricated Stewart Platform using CAD software and mechanical calculations.
\item To develop a force balance for the Stewart platform and obtain forces and moments measurement during model testing.
\item To obtain flow velocity measurement in the wind tunnel by use of pitot tubes.
\item To develop a Human-Machine Interface for measurement readings and control of the Stewart platform load balance.
\end{enumerate}
\subsection{Expected Outcomes}
\begin{enumerate}
\item A functional force balance for measuring the aerodynamic loads applied on a model
and for calculating aerodynamic coefficients from the measurements taken.
\item A velocity measurement system for the wind tunnel using pitot tubes.
\item A human machine interface with access to control of the Stewart platform electronics
and data acquisition from sensors.
\end{enumerate}

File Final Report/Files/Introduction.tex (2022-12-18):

\section{Introduction}
\label{sec:introduction}
Obtaining and simulating the aerodynamic performance of items in a wind tunnel is a
significant and important part in the development of vehicles, aircraft and other machines
that require aerodynamic performance evaluation. For most wind tunnel experiments where existing force balances are used,
it is only possible to alter the object's angle of attack by use of linear  actuators for example.
However, due to the complex manoeuvres that
may require simulation, there is a need for dynamic positioning of the model of the object
in the wind tunnel. A six-DOF Stewart platform can be used to achieve these dynamic positions and can be used as a force balance.
\subsection{Background}
A Stewart platform is a six degree-of-freedom mechanism that consists of a base and a platform connected with six legs. In some Stewart platforms,
each leg is connected to the ground by a two-axis joint and is provided with controllable means for extending its length
\cite{wittenburg2016stewart}. The six DOF Stewart Platform provides an elegant design for simulating flight conditions.\cite{stewart1965platform}.

The Stewart platform can be used in conjunction with wind tunnels for wind tunnel experiments. Wind tunnels are used to measure the aerodynamic forces on aeroplanes, wings, cars, trucks, bridges, and buildings. This can be done by positioning models of these vehicles in the tunnel's test section.
The Stewart platform can provide various dynamic positions to simulate complex vehicle manoeuvres. Incorporating a force balance with the Stewart platform will allow direct measurement of forces and torques acting on the model that is being tested in the wind tunnel.

For this project, the force balance is intended to be built as simple and accessible as possible. Thus, the use of a six DOF Stewart Platform as a force balance.
A Stewart Platform was fabricated in a previous final year project. However, a force balance was not integrated into it.
Electrical load measurement devices have to be connected to the legs of the Stewart platform in order to measure and obtain the results thus making it fully operational \cite{caleb}.

\subsection{Problem Environment}
Simulation and analysis of scaled models is an important step in the development of aircraft, vehicles and other machines. Such analysis provides aerodynamic performance data that can be used to inform any modifications or improvements e.g. in aircraft and vehicles to make them more efficient and safer. One such method that is used to perform aerodynamic performance evaluation is the wind tunnel used in conjunction with sensors for data acquisition by a computer. External or internal six-component force balances are also used. Another such technology that can be used for this purpose is the Stewart platform, which can be used to simulate the
orientation of vehicles and aircraft in the actual environment.

Whereas the force balances give very accurate results, some are expensive to build and use. Also, some objects require complex manoeuvre simulations to imitate the actual movements in air. There is therefore the need for dynamic positioning of objects in the wind tunnel.
\subsection{Problem Statement}
Measured parameters obtained in aerodynamic testing are critical in the development of parts. Current commercial force balances provide means to position models and obtained forces and moments during testing.
However, these force balances are quite expensive and some do not provide an integrated solution. There is therefore a need to develop a cost effective yet accurate force balance that can be used to for measurements at the Fluids lab in JKUAT. The platform should be able to measure 6 components of aerodynamic loading, as well as position the model within the wind tunnel with 6 degrees of freedom.
\subsection{Objectives}
\subsubsection{Main Objective}
\paragraph{} To develop a force balance and a control system for the Stewart platform.
\subsubsection{Specific Objectives}
\begin{enumerate}
    \item To develop a force balance for the Stewart platform and obtain forces and moments measurement during model testing.
    \item To obtain flow velocity measurement in the wind tunnel by use of pitot tubes.
    \item To develop a Human-Machine Interface for measurement readings and control of the Stewart platform load balance.
    \item To improve model behaviour visualization in the wind tunnel by introduction of smoke streamlines in the wind tunnel.
\end{enumerate}
\subsection{Expected Outcomes}
\begin{enumerate}
    \item A functional force balance for measuring the aerodynamic loads applied on a model and for calculating aerodynamic coefficients from the measurements taken.
    \item A velocity measurement system for the wind tunnel using pitot tubes.
    \item A human machine interface with access to control of the Stewart platform electronics and data acquisition from sensors.
    \item A smoke generation and visualization assembly incorporated into the wind tunnel.
\end{enumerate}

\subsection{Justification}
In a large percentage of cases, the measurement of forces and moments experienced by
a model during wind tunnel testing is critical. To achieve this in a cost sustainable way
while allowing the dynamic positioning of model for different test cases is important for
development of aerodynamic bodies and parts. In many cases where both these goals are
achieved, it results in expensive and hard to maintain devices or integrated wind tunnels.

This high cost of wind tunnel force balances limits educational access to study areas around
 the scientific study in aerodynamics for aeronautical and automotive applications. Lowering 
the cost of force balances would increase access to studies in these fields and inspire
 students to participate in STEM, especially in low-income areas/countries.

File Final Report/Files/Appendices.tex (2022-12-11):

\appendix
%\addcontentsline{toc}{section}{Appendices}
\section{Appendices}
\pagenumbering{roman}
\subsection{Stewart Platform and Wind Tunnel Configurations}
\includepdf[pages=-]{Wind Tunnel Assembly + Stewart}
\includepdf[pages=-]{Assemby 3 2}
\clearpage
\subsection{Budget and TimePlan}
\subsubsection{Provisional Budget}
\begin{center}
	\begin{table}[H]
		\centering
		\caption{Proposed budget}
		\paragraph{ }
		
	\end{table}
\end{center}
\subsubsection{Work Plan}
\begin{center}
	\begin{table}[H]
		\centering
		\caption[Time plan]{Time plan for first and second semester}
		\paragraph{ }
		
	\end{table}
\end{center}
\clearpage
\subsection{Production Plan}
\includepdf[pages=-]{Production plan}

\clearpage

\subsection{Force transformation matrix}
In such a case the forces experienced at the top of the platform are distributed between the 6 legs and as result, a force transformation matrix is required to resolve the forces applied on each axis as measured by each load cell on each leg.

If the platform is acted upon by an external wrench {$\vec{F}_e, \vec{M}_e$}, for static equilibrium of the body, the external wrench is statically balanced by the six leg forces of the Stewart platform. Representing the unit vector $\hat{I}_i$ along the i-th leg with respect to B, the leg force is given  by $\hat{I}_if_i$. Considering the force equilibrium of the platform along  three mutually perpendicular directions in B(XYZ), the following force equations can be obtained as in \cite{dwarakanath_design_2001}:

\begin{ceqn}
	\begin{align}
		(F_e)_x = f_1I_{1x} + f_2I_{2x} + f_3I_{3x} + f_4I_{4x} + f_5I_{5x} + f_6I_{6x}
	\end{align}
\end{ceqn}
\begin{ceqn}
	\begin{align}
		(F_e)_y = f_1I_{1y} + f_2I_{2y} + f_3I_{3y} + f_4I_{4y} + f_5I_{5y} + f_6I_{6y}
	\end{align}
\end{ceqn}
\begin{ceqn}
	\begin{align}
		(F_e)_z = f_1I_{1z} + f_2I_{2z} + f_3I_{3z} + f_4I_{4z} + f_5I_{5z} + f_6I_{6z}
	\end{align}
\end{ceqn}
where $(F_e)_x$, $(F_e)_y$ and $(F_e)_z$ are the external forces on the platform along three mutually perpendicular directions x, y and z of the frame B, respectively.

The moment due to the forces $\hat{I}_if_i$ about the origin of B is $(\vec{b}_i x \hat{I}_i)f_i$. Considering the moment equilibrium about x, y and z axes of B, the following moment equations can be obtained as in \cite{dwarakanath_design_2001}:

\begin{ceqn}
	\begin{align}
		(M_e)_x = f_1(\vec{b}_1 x \hat{I}_1)_x + f_2(\vec{b}_2 x \hat{I}_2)_x + f_3(\vec{b}_3 x \hat{I}_3)_x + f_4(\vec{b}_4 x \hat{I}_4)_x + f_5(\vec{b}_5 x \hat{I}_5)_x + f_6(\vec{b}_6 x \hat{I}_6)_x
	\end{align}
\end{ceqn}
\begin{ceqn}
	\begin{align}
		(M_e)_y = f_1(\vec{b}_1 x \hat{I}_1)_y + f_2(\vec{b}_2 x \hat{I}_2)_y + f_3(\vec{b}_3 x \hat{I}_3)_y + f_4(\vec{b}_4 x \hat{I}_4)_y + f_5(\vec{b}_5 x \hat{I}_5)_y + f_6(\vec{b}_6 x \hat{I}_6)_y
	\end{align}
\end{ceqn}
\begin{ceqn}
	\begin{align}
		(M_e)_z = f_1(\vec{b}_1 x \hat{I}_1)_z + f_2(\vec{b}_2 x \hat{I}_2)_z + f_3(\vec{b}_3 x \hat{I}_3)_z + f_4(\vec{b}_4 x \hat{I}_4)_z + f_5(\vec{b}_5 x \hat{I}_5)_z + f_6(\vec{b}_6 x \hat{I}_6)_z
	\end{align}
\end{ceqn}

where $(M_e)_x$, $(M_e)_y$ and $(M_e)_z$ are the external moments on the platform  about the three coordinate axes of B. Combining the equations the relationship between the external wrench and the forces experienced by the legs can be expressed as follows:
\begin{ceqn}
	\begin{align}
		\begin{Bmatrix}
			\vec{F}_e \\
			\vec{M}_e \\
		\end{Bmatrix} = [H]\{F\}
	\end{align}
\end{ceqn}
\clearpage
\subsection{Code}
The complete firmware and HMI programs can be found in this repository,

https://github.com/SammyOina/stewart-platform.
\clearpage

\subsection{PCB schematics}
\subsubsection{schematics}
\includepdf[pages=-]{Figures/schm}

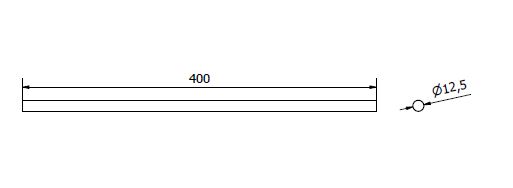
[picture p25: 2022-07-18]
Final Report/Figures/Strut.JPG

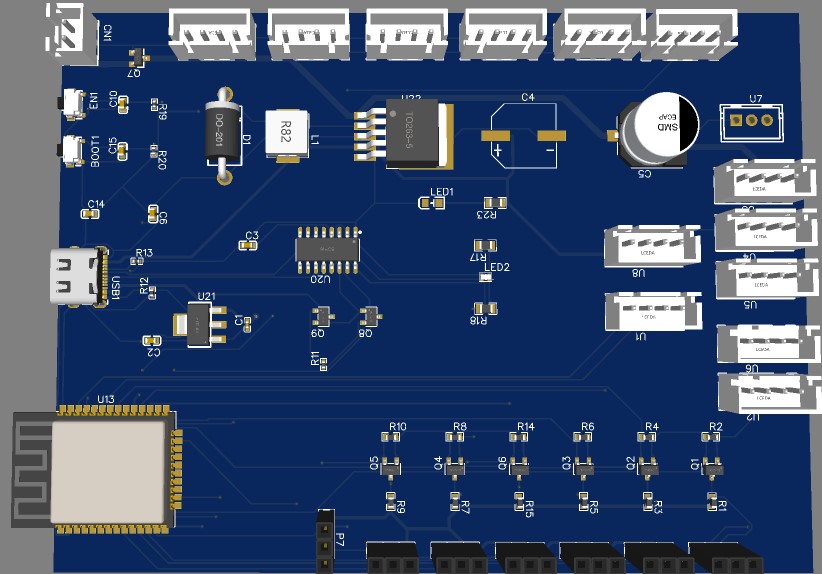
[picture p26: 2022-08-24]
Final Report/Figures/pcb.jpg

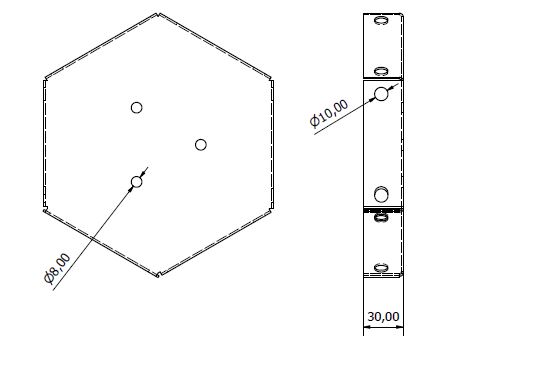
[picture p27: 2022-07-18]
Final Report/Figures/Folded.JPG

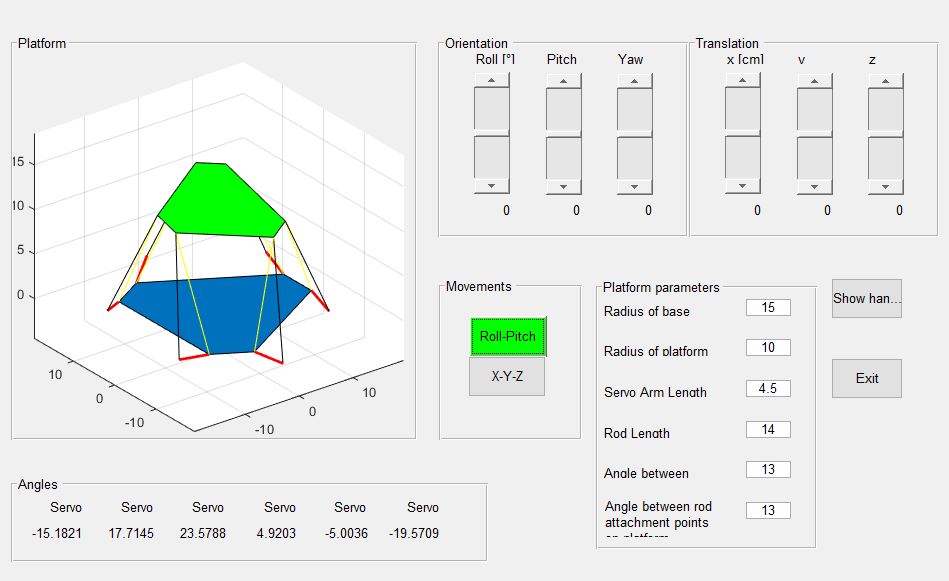
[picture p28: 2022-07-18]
Final Report/Figures/Matlab2.JPG

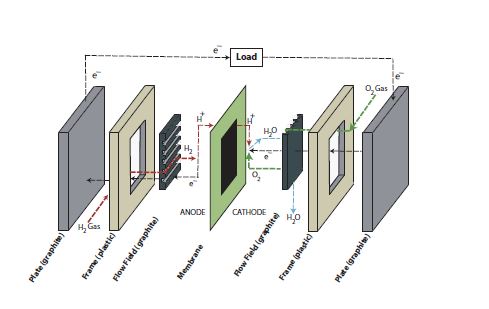
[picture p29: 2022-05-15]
Final Report/Figures/Figure5.JPG

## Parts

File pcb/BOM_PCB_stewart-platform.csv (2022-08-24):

ID | Name | Designator | Footprint | Quantity | Manufacturer Part | Manufacturer | Supplier | Supplier Part | Price
1 | 1TS003B-1800-3500A | BOOT1,EN1 | SW-SMD_1TS003B-XXXX-3500A-CT | 2 | 1TS003B-1800-3500A | HYP | LCSC | C255809 | 0.039
2 | 10uF | C1 | C0402 | 1 | CL05A106MQ8NUB8 | Samsung Electro-Mechanics | LCSC | C307416 | 0.046
3 | 0.1uF | C2,C3,C6,C10,C14,C15 | C0603 | 6 | 0603B104K250 | WTC | LCSC | C83054 | 0.003
4 | 220uF | C4 | CAP-SMD_BD10.0-L10.3-W10.3-LS11.3-FD | 1 | UCD1H221MNL1GS | Nichicon | LCSC | C116211 | 0.296
5 | 680uF | C5 | CAP-SMD_BD10.0-L10.3-W10.3-LS11.0-R-RD | 1 | VEJ681M1CTR-1010 | LELON | LCSC | C134782 | 0.187
6 | B2B-XH-A (LF)(SN) | CN1 | CONN-TH_B2B-XH-A-LF-SN | 1 | - | JST Sales America | LCSC | C158012 | 0.065
7 | SS34_C8678 | D2 | DO-214AC_L4.3-W2.7-LS5.3-RD | 1 | SS34 | MDD | LCSC | C8678 | 0.031
8 | 33uH | L1 | IND-SMD_L7.0-W6.6_FXL0630 | 1 | MCW-0630-330-N2 | Hk-hotline | LCSC | C177254 | 0.282
9 | 17-21/BHC-XL2M2TY/3T | LED1 | LED0805-RD | 1 | 17-21/BHC-XL2M2TY/3T | EVERLIGHT | LCSC | C72035 | 0.035
10 | 18-225/B6R6C-C01/3T | LED2 | LED-SMD_4P-L1.6-W0.8-BR-RD | 1 | 18-225/B6R6C-C01/3T | Everlight Elec | LCSC | C282127 | 0.079
11 | Header Female 2.54mm 1x3 | P1,P2,P3,P4,P5,P6,P7 | HEADER FEMALE 2.54MM 3X1 | 7 | Header-Female-2.54_1x3 | Boom Precision Elec | LCSC | C146243 | 0.056
12 | BSS138P,215 | Q1,Q2,Q3,Q4,Q5,Q6 | SOT-23-3_L2.9-W1.6-P1.90-LS2.8-BR | 6 | BSS138P,215 | Nexperia | LCSC | C75547 | 0.314
13 | BC817-40 | Q8,Q9 | SOT-23-3_L2.9-W1.6-P1.90-LS2.8-BR | 2 | BC817-40 | Hottech | LCSC | C181151 | 0.014
14 | 10K | R1,R2,R3,R4,R5,R6,R7,R8,R9,R10,R14,R15 | R0603 | 12 | 0603WAF4701T5E | UniOhm | LCSC | C23162 | 0.001
15 | 10K | R11,R19,R20 | R0402 | 3 | 0402WGJ0103TCE | UniOhm | LCSC | C25531 | 0.001
16 | 5.1K | R12,R13 | R0402 | 2 | 0402WGF5101TCE | UniOhm | LCSC | C25905
17 | 1K | R17,R18,R23 | R0805 | 3 | PTFR0805B1K00N9 | ResistorToday | LCSC | C328437 | 0.118
18 | B4B-XH-A(LF)(SN) | U1,U2,U3,U4,U5,U6,U8,U9,U10,U12,U14,U16,U18 | CONN-TH_B4B-XH-A-LF-SN | 13 | B4B-XH-A(LF)(SN) | JST Sales America | LCSC | C144395 | 0.058
19 | B3B-XH-A(LF)(SN) | U7 | CONN-TH_3P-P2.50_B3B-XH-A-LF-SN | 1 | B3B-XH-A(LF)(SN) | JST Sales America | LCSC | C144394 | 0.042
20 | ESP32-WROOM-32E(8MB) | U13 | WIFI-SMD_ESP32-WROOM-32E | 1 | ESP32-WROOM-32E(8MB) | Espressif Systems | LCSC | C701342 | 4.175
21 | CH340C | U20 | SOP-16_L10.0-W3.9-P1.27-LS6.0-BL | 1 | CH340C | WCH | LCSC | C84681 | 0.469
22 | AMS1117-3.3_C347222 | U21 | SOT-223_L6.7-W3.5-P2.30-BR | 1 | AMS1117-3.3 | Youtai Semiconductor Co., Ltd. | LCSC | C347222 | 0.05
23 | LM2596S-5.0/TR | U22 | TO-263-5_L10.2-W8.6-P1.70-LS14.4-TL | 1 | LM2596S-5.0/TR | HGSEMI | LCSC | C194349 | 0.669
24 | TYPE-C-31-M-09 | USB1 | USB-C-SMD_TYPE-C-31-M-09 | 1 | TYPE-C-31-M-09 | 韩国韩荣 | LCSC | C2689967 | 0.449

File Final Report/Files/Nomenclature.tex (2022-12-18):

\section*{Nomenclature}
    A - Cross-section area\\
    a - Diameter of moving\\
    b - Diameter of base\\
    B - coordinate system defined at centre of base plate\\
    COG - Center of Gravity\\
    d - length of rod\\
    DAQ/DAQA - Data Acquisition System\\
    DOF - Degrees of Freedom\\
    E - Young's Modulus\\
    EASA - East Africa School of Aviation\\
    ELB - Engineering Laboratory Building\\
    F - Axial Force\\
    FEA - Finite Element Analysis\\
    G - Modulus of rigidity\\
    $H$ - transformation matrix which related measured forces and applied forces\\
    h - height between base plate and moving platform\\
    HMI - Human Machine Interface\\
    I2C - Inter-Integrated Circuit\\
    J - Jacobian Matrix\\
    JKUAT - Jomo Kenyatta University of Agriculture and Technology\\
    NASA - National Space Agency\\
    RS - Recommended Standard\\
    SCL - Serial Clock\\
    SDA - Serial Data\\
    SPI - Serial Peripheral Interface\\
    TTL - Transistor-Transistor Logic\\
    UDP - User Datagram Protocol
%\pagebreak
%\paragraph{List of Symbols
%\begin{itemize}
%\item $\vec{b}_i$ - position of ith connection point at base with respect to B
%\item $\vec{F}_e$ - external force applied to platform
%\item $f_i$ - force exerted on ith leg due $F_e, M_e$
%\item $F$ - vector of leg forces
%\item $\hat{I}_i$ - Unit vector along the ith leg
%\item $\vec{M}_e$ - external moment applied to platform
%\item $\hat{{S_{i}}}$ - unit vector of the Plucker coordinates
%\item $\alpha$ - Angle of attack
%\item $\beta$ - Side slip angle
%\item $|J|$ - determinant of Jacobian matrix
%\item $|J|_{m}$ - determinant of Jacobian matrix of optimal Stewart PLatform configuration
%\item $\lambda$ - Quality index
%\end{itemize}}

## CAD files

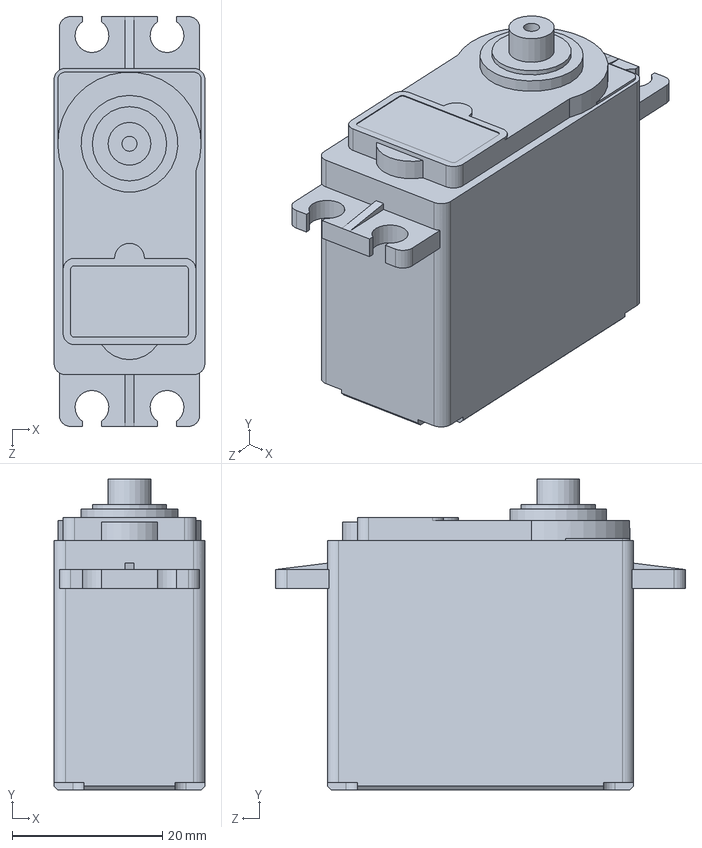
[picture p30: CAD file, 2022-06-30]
CAD/ServoMotor/GRAB_CAD_MODELS/SERVO_MOTOR/FeeTech FS5109M Metal Gear Servo Outer volume.SLDPRT
20.1 x 41.4 x 54.6 mm

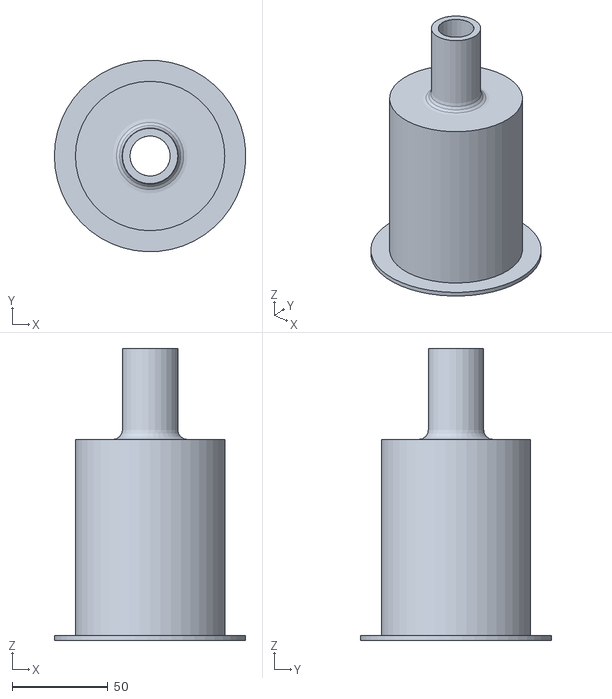
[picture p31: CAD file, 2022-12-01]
CAD/Smoke generator/Smoke connector ready.stl
99.9 x 99.9 x 152.5

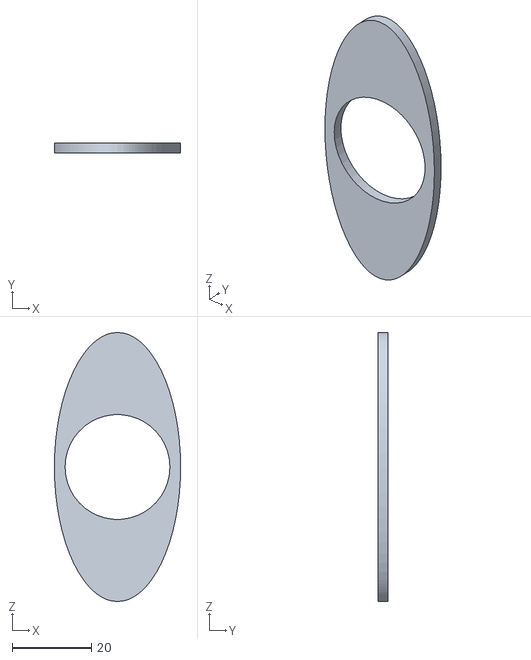
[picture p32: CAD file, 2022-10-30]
CAD/Smoke generator/Smoke visualization bottom.stl
31.9 x 2.50 x 68.0

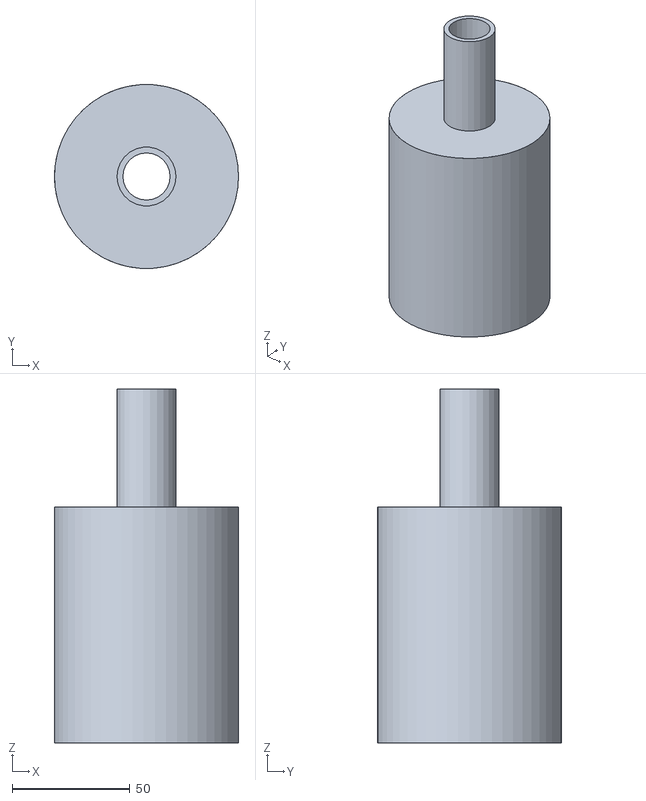
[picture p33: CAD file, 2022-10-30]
CAD/Smoke generator/Smoke connector.stl
78.0 x 78.0 x 150.0

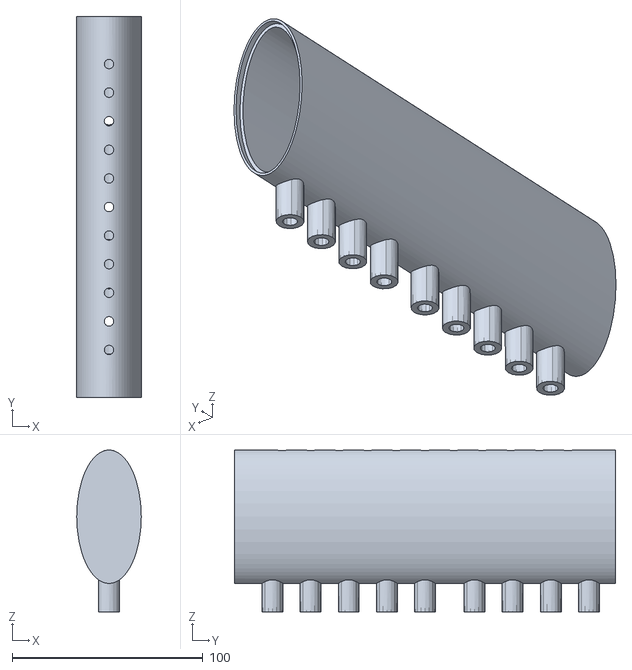
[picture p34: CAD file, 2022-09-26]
CAD/Smoke generator/Smoke visualization device.stl
33.9 x 200.0 x 85.0

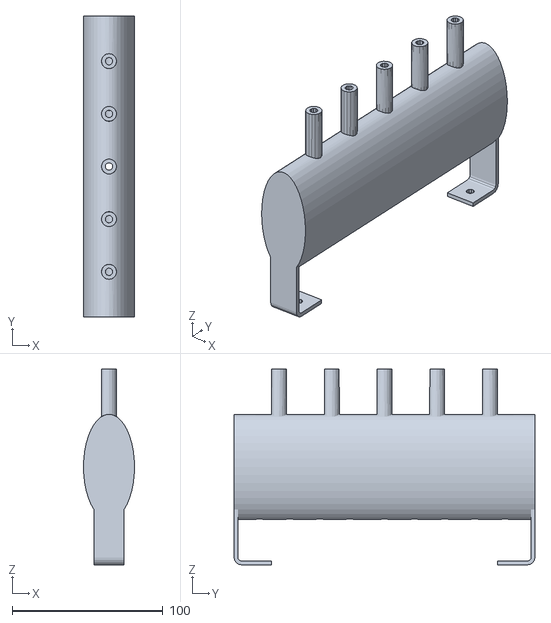
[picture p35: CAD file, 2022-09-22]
CAD/Smoke generator/Streamline smoke.stl
33.9 x 200.0 x 130.0

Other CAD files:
CAD/Smoke generator/Assembly1.dwg
CAD/Spherical joint/Assembly1.dwg
CAD/Wind tunnel/TEST SECTION/updatedtestsectionassembly + Platform.dwg
CAD/Wind tunnel/Wind Tunnel Assembly 1.dwg
CAD/Smoke generator/Assembly2.dwg
CAD/Assemby 3 (1).dwg
CAD/Test flange.dwg
CAD/Moving platform.dwg
CAD/Servo horn.dwg
CAD/Drawing2.dwg
CAD/Rod qty-6 Not hollow.dwg
CAD/Strut.dwg
CAD/Adapter shaft.ipt
CAD/Assembly2.iam
CAD/Assemby 3.dwg
CAD/Assemby 3.iam
CAD/Assemby 3.stp
CAD/Bottom plate 2.5mm.dwg
CAD/Bottom plate 2.5mm.ipt
CAD/Ideation 1.dwg
CAD/Ideation 1.ipt
CAD/Ideation.ipt
CAD/Moving platform - Flat pattern.dwg
CAD/Moving platform and legs.iam
CAD/Moving platform.ipt
CAD/OldVersions/Assembly2.0004.iam
CAD/OldVersions/Assemby 3.0016.iam
CAD/OldVersions/Bottom plate 2.5mm.0003.ipt
CAD/OldVersions/Moving platform and legs.0006.iam
CAD/OldVersions/Moving platform.0001.dwg
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

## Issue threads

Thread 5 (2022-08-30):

### ISSUE TITLE
PCB Review

### ISSUE THREAD

**Issue by rodneyosodo** [SammyOina/stewart-platform#5]
# 
![Screenshot from 2022-08-24 15-43-25](https://user-images.githubusercontent.com/28790446/186422255-f87652d3-38ab-4aac-a0b1-dd23ac016be4.png)

- I'd suggest you have the via diameter equal to track width
- Increase clearance for Default
- Check on minimum clearance and minimum via diameter from JLCPCB

# 
![Screenshot from 2022-08-24 15-42-26](https://user-images.githubusercontent.com/28790446/186422279-030e6552-edb5-4152-b5cb-ce158c8f206f.png)

- You can use smd diode, resisitor and also capacitor

#
![Screenshot from 2022-08-24 15-42-08](https://user-images.githubusercontent.com/28790446/186422288-3545ad40-92a6-4040-8c9f-4c6adeb072ca.png)

- you can place the MCU in the middle and add a ground plane beneath it or even remove PCB so as it has a huge hole

#
![Screenshot from 2022-08-24 15-40-05](https://user-images.githubusercontent.com/28790446/186422309-8330d09e-9b3d-4f87-8cf2-96757f763b0d.png)

- What are these for?

#
![Screenshot from 2022-08-24 15-38-34](https://user-images.githubusercontent.com/28790446/186422322-8519adb9-3ff3-4b39-85e5-cf5193cdf158.png)

- Align the net labels and names
#
![Screenshot from 2022-08-24 15-37-54](https://user-images.githubusercontent.com/28790446/186422351-ecf1575f-192d-4670-877d-a2686a601721.png)

- you can add a bulk capacitor
#
![Screenshot from 2022-08-24 15-37-34](https://user-images.githubusercontent.com/28790446/186422380-bfecdc8d-29a8-45c3-9039-c2aa51465bce.png)

- Do you need this because your connector is JST and it only goes one way or which connector are you using?
- Don't you need a resistor

**Comment by SammyOina** [comment]
"you can place the MCU in the middle and add a ground plane beneath it or even remove PCB so as it has a huge hole"
Didn't want to interfere with the antenna, does the ground plane beneath the MCU interfere with signals @0x6f736f646f

**Comment by SammyOina** [comment]
Do you need this because your connector is JST and it only goes one way or which connector are you using?
Don't you need a resistor

I'll get rid of it cause I'm using JST

**Comment by SammyOina** [comment]
You can use smd diode, resisitor and also capacitor

only the diode is not smt

**Comment by SammyOina** [comment]
you can add a bulk capacitor

is it necessary @0x6f736f646f  cause I have some capacitors on the buck converter

**Comment by SammyOina** [comment]
What are these for?

the i2c bus is just for extra I/O

**Comment by rodneyosodo** [comment]
> "you can place the MCU in the middle and add a ground plane beneath it or even remove PCB so as it has a huge hole" Didn't want to interfere with the antenna, does the ground plane beneath the MCU interfere with signals @0x6f736f646f

No. If they are signal wires underneath yes.

**Comment by rodneyosodo** [comment]
> You can use smd diode, resisitor and also capacitor
> 
> only the diode is not smt

How so? What diode is it?

**Comment by rodneyosodo** [comment]
> you can add a bulk capacitor
> 
> is it necessary @0x6f736f646f cause I have some capacitors on the buck converter

Not necessary but a good enhancement

**Comment by rodneyosodo** [comment]
> What are these for?
> 
> the i2c bus is just for extra I/O

Why not one?

**Comment by SammyOina** [comment]
> > "you can place the MCU in the middle and add a ground plane beneath it or even remove PCB so as it has a huge hole" Didn't want to interfere with the antenna, does the ground plane beneath the MCU interfere with signals @0x6f736f646f
> 
> No. If they are signal wires underneath yes.

In that case I'll just leave it there

**Comment by SammyOina** [comment]
> > You can use smd diode, resisitor and also capacitor
> > only the diode is not smt
> 
> How so? What diode is it?

the diode was 1N5822 I have replaced it with SS34 in https://github.com/SammyOina/stewart-platform/commit/a19fa3e659def1261903ad4870dcb75b86429917

**Comment by SammyOina** [comment]
> > you can add a bulk capacitor
> > is it necessary @0x6f736f646f cause I have some capacitors on the buck converter
> 
> Not necessary but a good enhancement

any suggestion on suitable capacitance

**Comment by SammyOina** [comment]
> > What are these for?
> > the i2c bus is just for extra I/O
> 
> Why not one?

Just a redundancy now removed in https://github.com/SammyOina/stewart-platform/commit/86757a8a3ff919bb4a3457589e3a49e60fa6ca65

**Comment by rodneyosodo** [comment]
> > > "you can place the MCU in the middle and add a ground plane beneath it or even remove PCB so as it has a huge hole" Didn't want to interfere with the antenna, does the ground plane beneath the MCU interfere with signals @0x6f736f646f
> > 
> > 
> > No. If they are signal wires underneath yes.
> 
> In that case I'll just leave it there

You can place it at the centre of one of the edges

**Comment by rodneyosodo** [comment]
> > > you can add a bulk capacitor
> > > is it necessary @0x6f736f646f cause I have some capacitors on the buck converter
> > 
> > 
> > Not necessary but a good enhancement
> 
> any suggestion on suitable capacitance

470uF

**Comment by rodneyosodo** [comment]
Add mounting holes on the PCB

**Comment by SammyOina** [comment]
> Add mounting holes on the PCB

I'll add that as well as silk screens before making the order, just wanted to ensure functionality

**Comment by SammyOina** [comment]
> > > > "you can place the MCU in the middle and add a ground plane beneath it or even remove PCB so as it has a huge hole" Didn't want to interfere with the antenna, does the ground plane beneath the MCU interfere with signals @0x6f736f646f
> > > 
> > > 
> > > No. If they are signal wires underneath yes.
> > 
> > 
> > In that case I'll just leave it there
> 
> You can place it at the centre of one of the edges

It's in that position just cause of routing but I'll optimize and try to move it before making the order

**Comment by rodneyosodo** [comment]
> > Add mounting holes on the PCB
> 
> I'll add that as well as silk screens before making the order, just wanted to ensure functionality

Isn't silk screen already added?

**Comment by SammyOina** [comment]
> > > Add mounting holes on the PCB
> > 
> > 
> > I'll add that as well as silk screens before making the order, just wanted to ensure functionality
> 
> Isn't silk screen already added?

Yes, Just editing them and making sure everything is in place, which is now done

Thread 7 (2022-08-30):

### ISSUE TITLE
Ground and power connections.

### ISSUE THREAD

**Issue by kimanimichael** [SammyOina/stewart-platform#7]
![Screenshot from 2022-08-29 19-23-46](https://user-images.githubusercontent.com/49106674/187248863-13b9f5f6-0987-4e72-8b4a-1a2932185884.png)

Any reason for introducing the above inconsistency? If not, I'd advise you maintain the conventional ground symbol.

Also I'd advise to maintain all power connections as you have done above for the 12V. Makes reviewing easier.

**Comment by SammyOina** [comment]
It's just included the Net port and net flag just for the appearance as they fit in some connections aesthetically, otherwise I agree on the point about consistency

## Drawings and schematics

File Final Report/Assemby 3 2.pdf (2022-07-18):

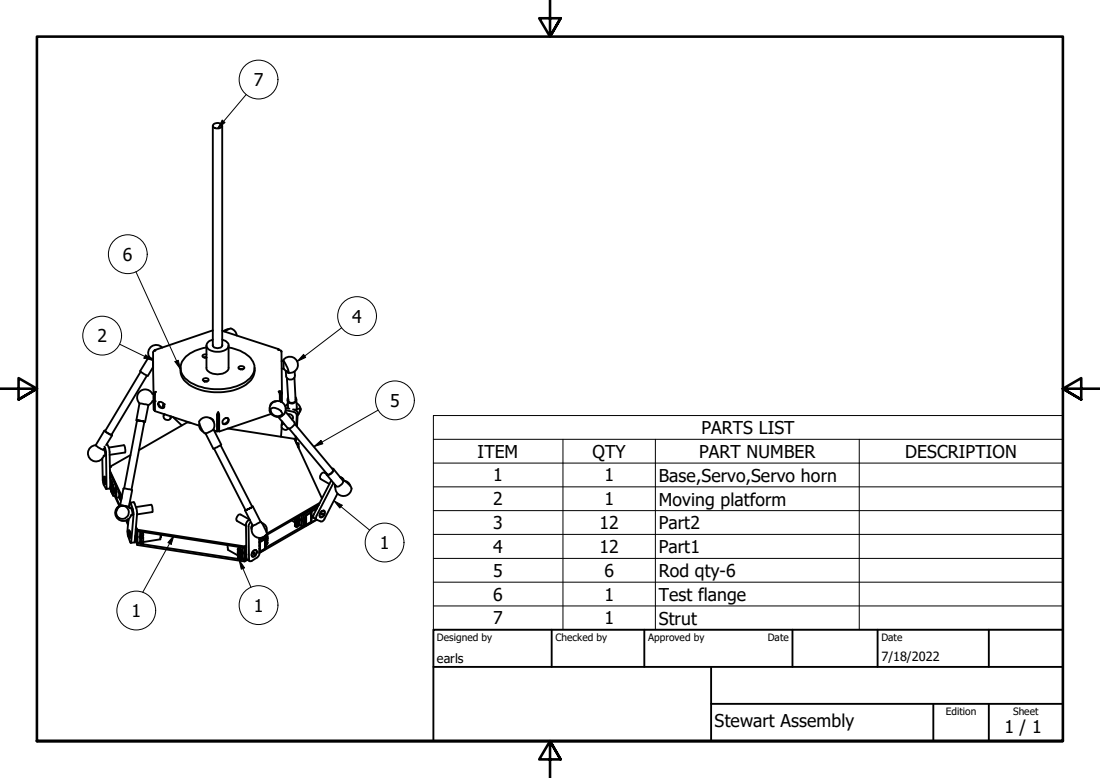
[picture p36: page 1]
PARTS LIST; Stewart Assembly

ITEM | QTY | PART NUMBER | DESCRIPTION
1 | 1 | Base,Servo,Servo horn
2 | 1 | Moving platform
3 | 12 | Part2
4 | 12 | Part1
5 | 6 | Rod qty-6
6 | 1 | Test flange
7 | 1 | Strut

Designed by earls | Checked by | Approved by Date | | Date 7/18/2022

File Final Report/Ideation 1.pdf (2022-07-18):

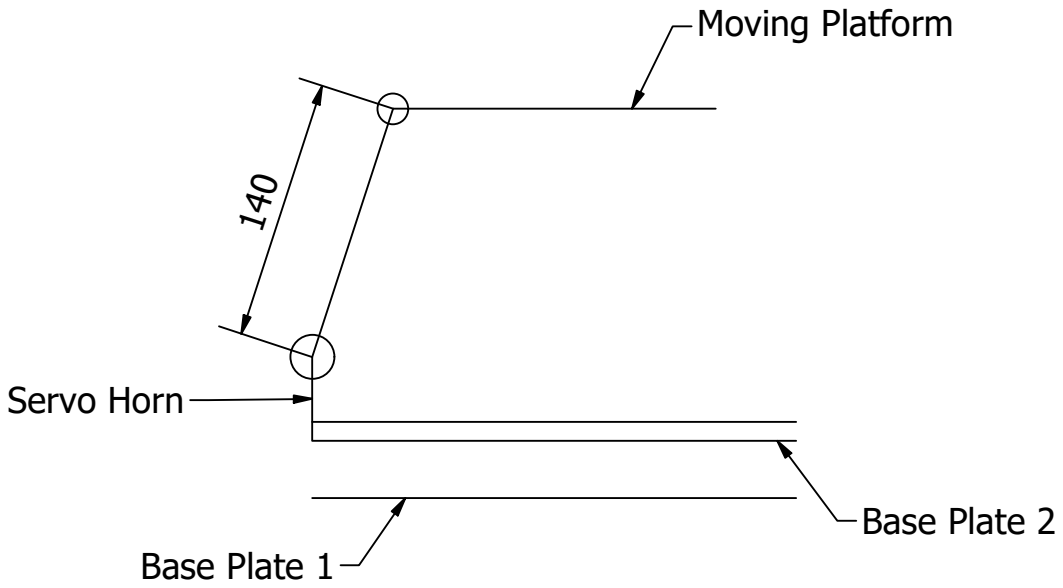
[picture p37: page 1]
Designed by; Checked by; Approved by; Date; Base Plate 1; Base Plate 2; Moving Platform; Servo Horn

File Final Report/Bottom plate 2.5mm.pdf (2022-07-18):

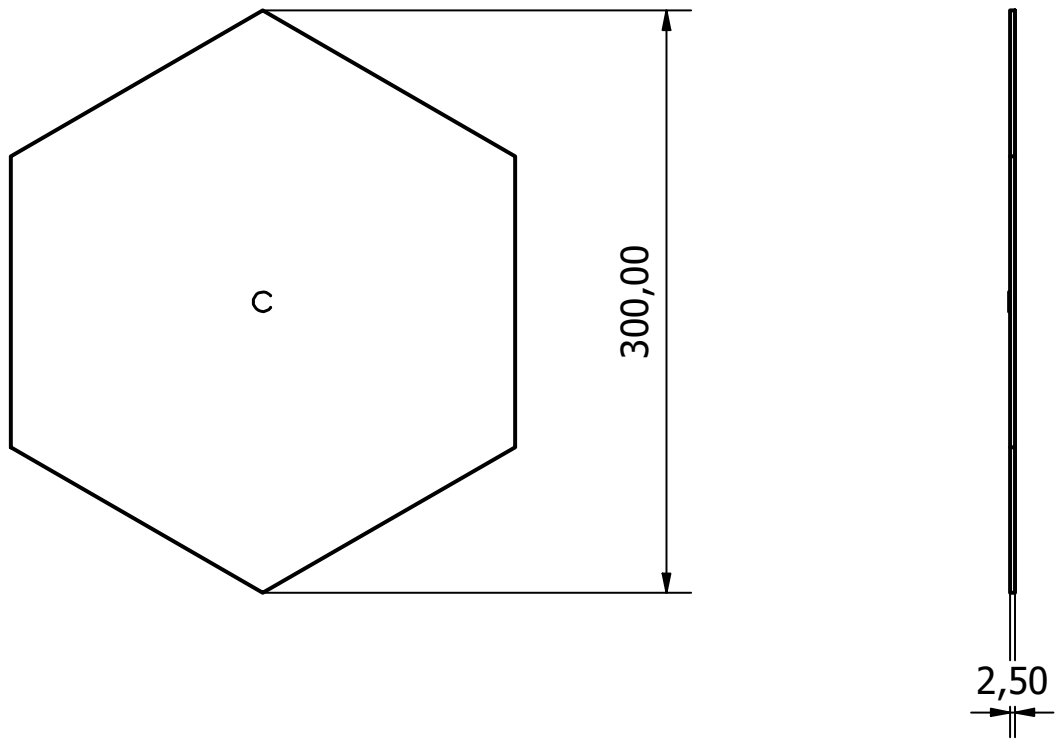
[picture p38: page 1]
Bottom plate 2.5mm; Designed by; Checked by; Approved by; Date

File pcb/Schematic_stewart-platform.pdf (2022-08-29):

# U13GND ³⁹

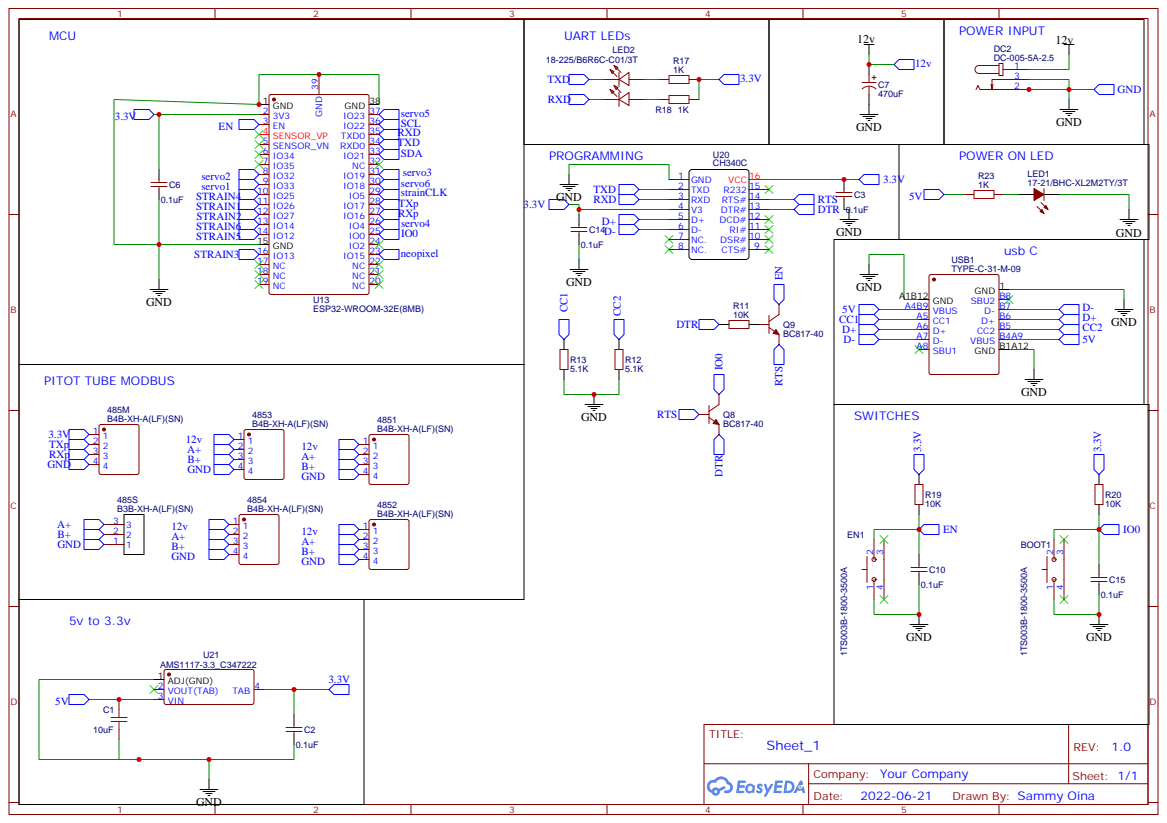
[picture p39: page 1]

Drawn By: Sammy Oina

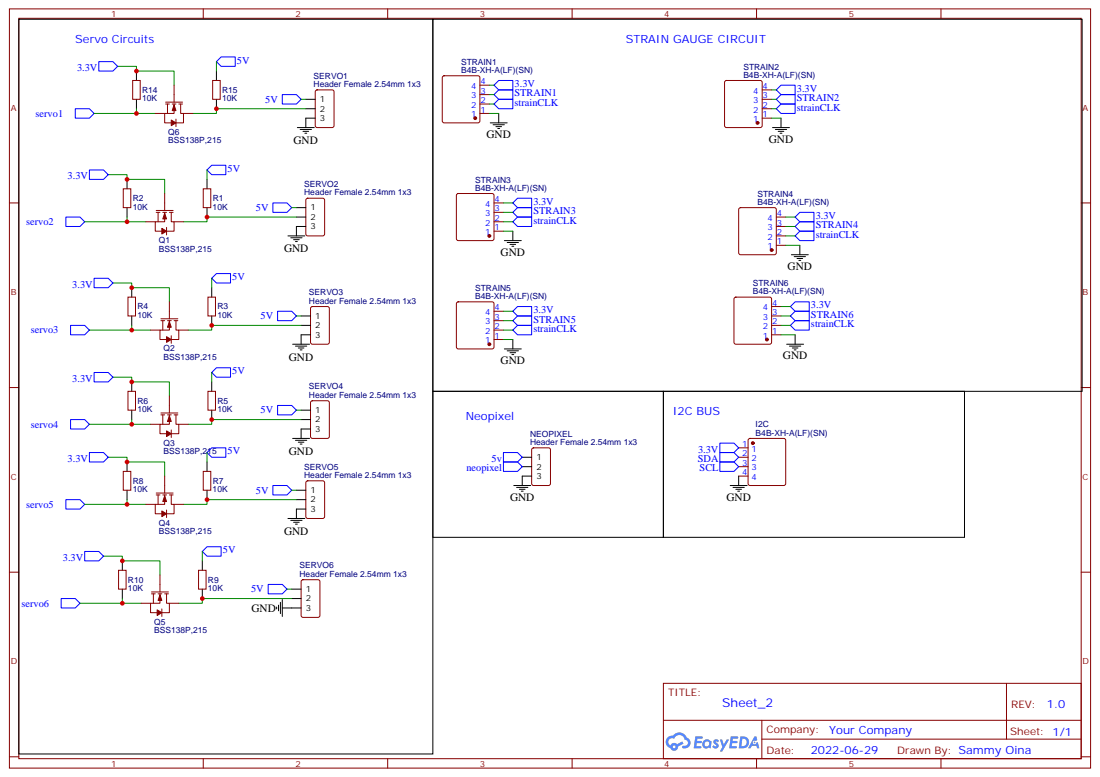
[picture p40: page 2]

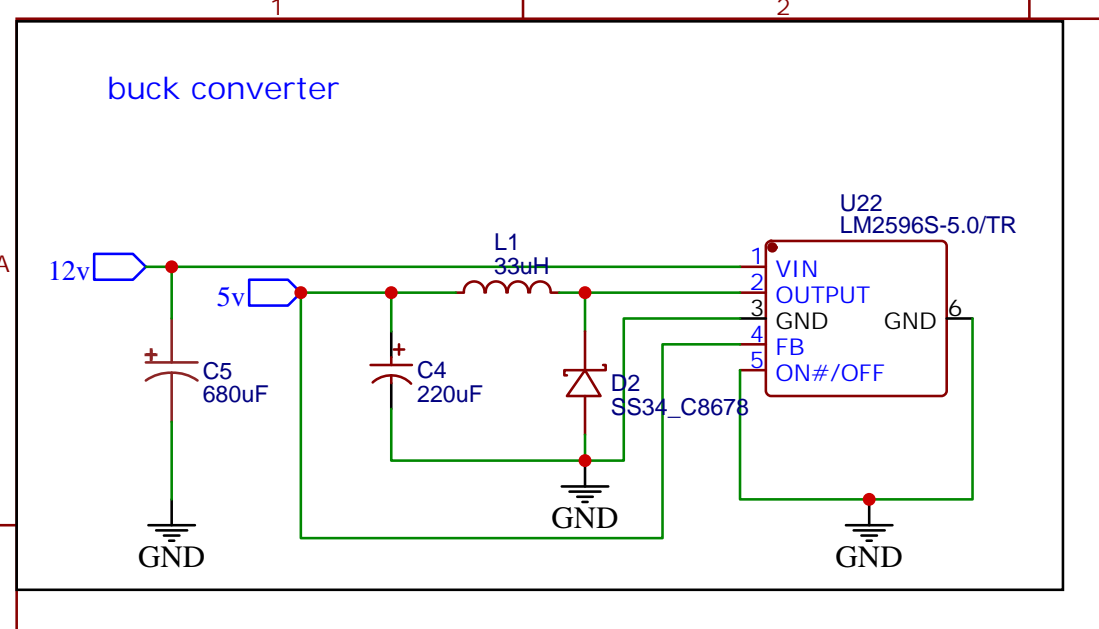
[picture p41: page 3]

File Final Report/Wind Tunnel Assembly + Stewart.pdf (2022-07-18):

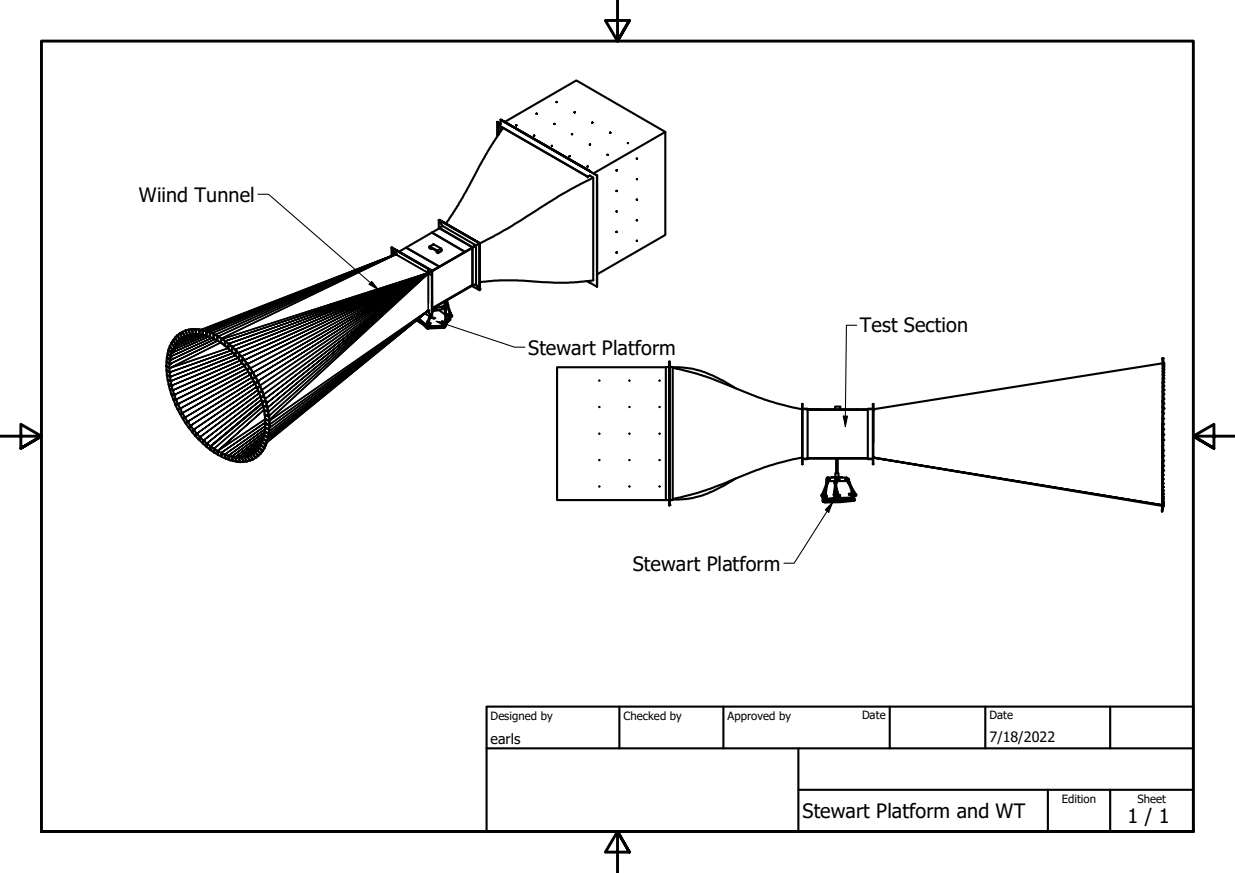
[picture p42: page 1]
Designed by; Checked by; Approved by; Date; Test Section; Stewart Platform; Wiind Tunnel

Stewart Platform and WT

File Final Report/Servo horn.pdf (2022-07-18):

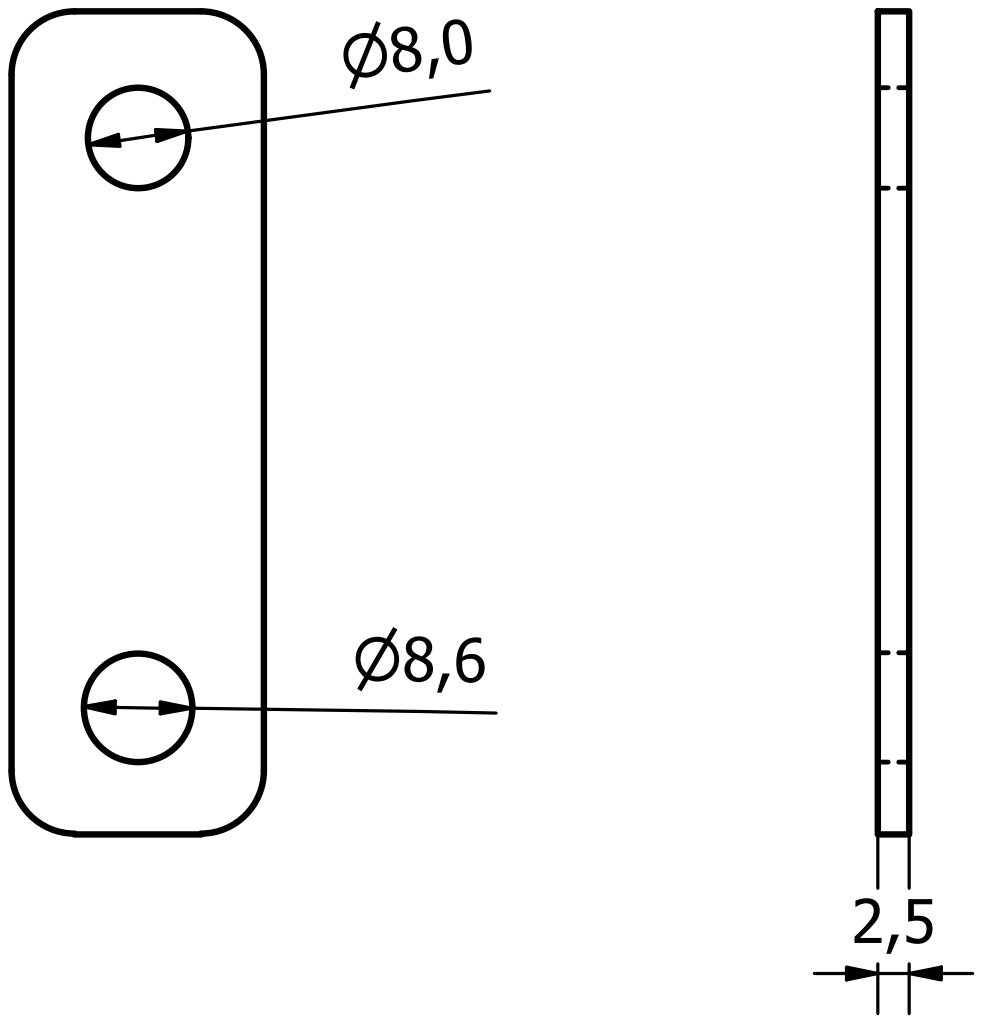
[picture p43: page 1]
Designed by; Checked by; Approved by; Date

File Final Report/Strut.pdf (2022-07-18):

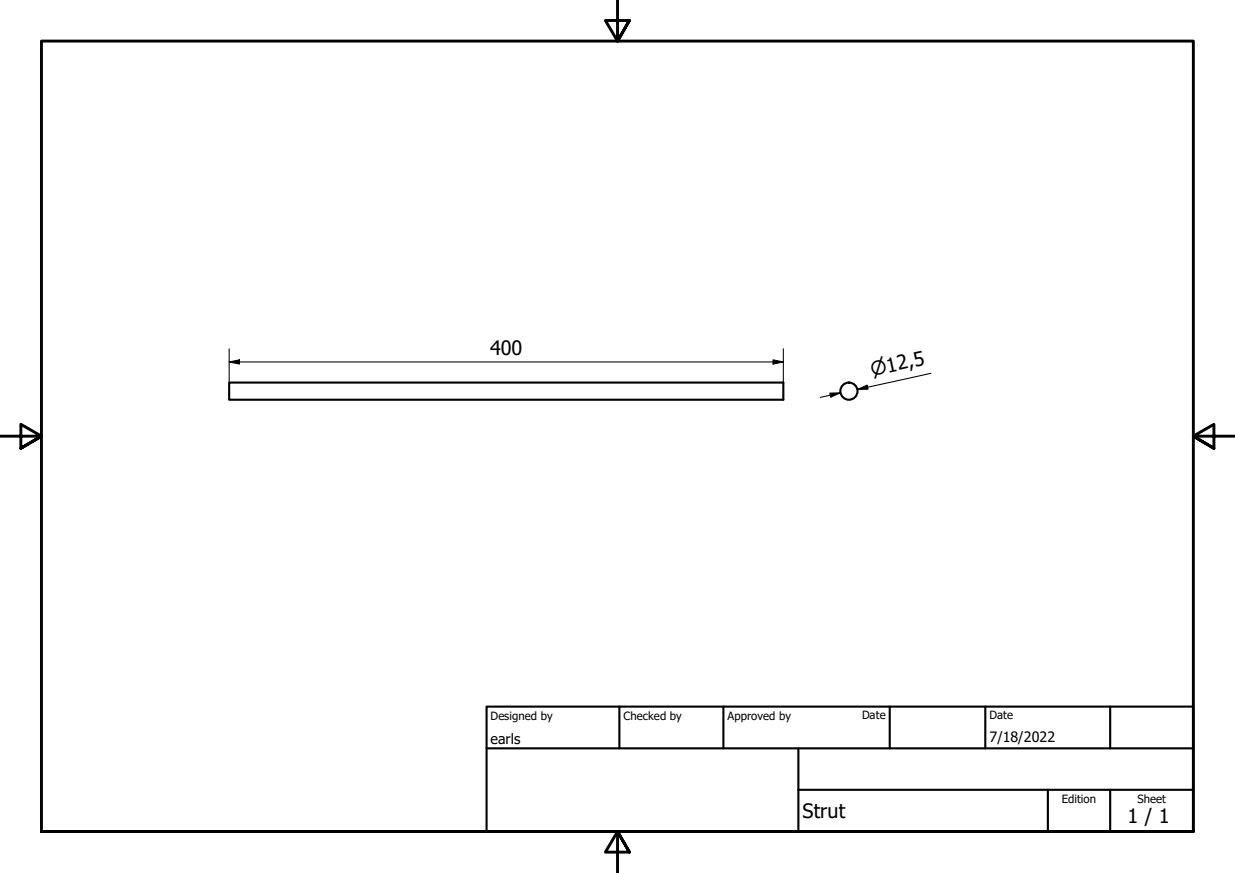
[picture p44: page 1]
Designed by; Checked by; Approved by; Date

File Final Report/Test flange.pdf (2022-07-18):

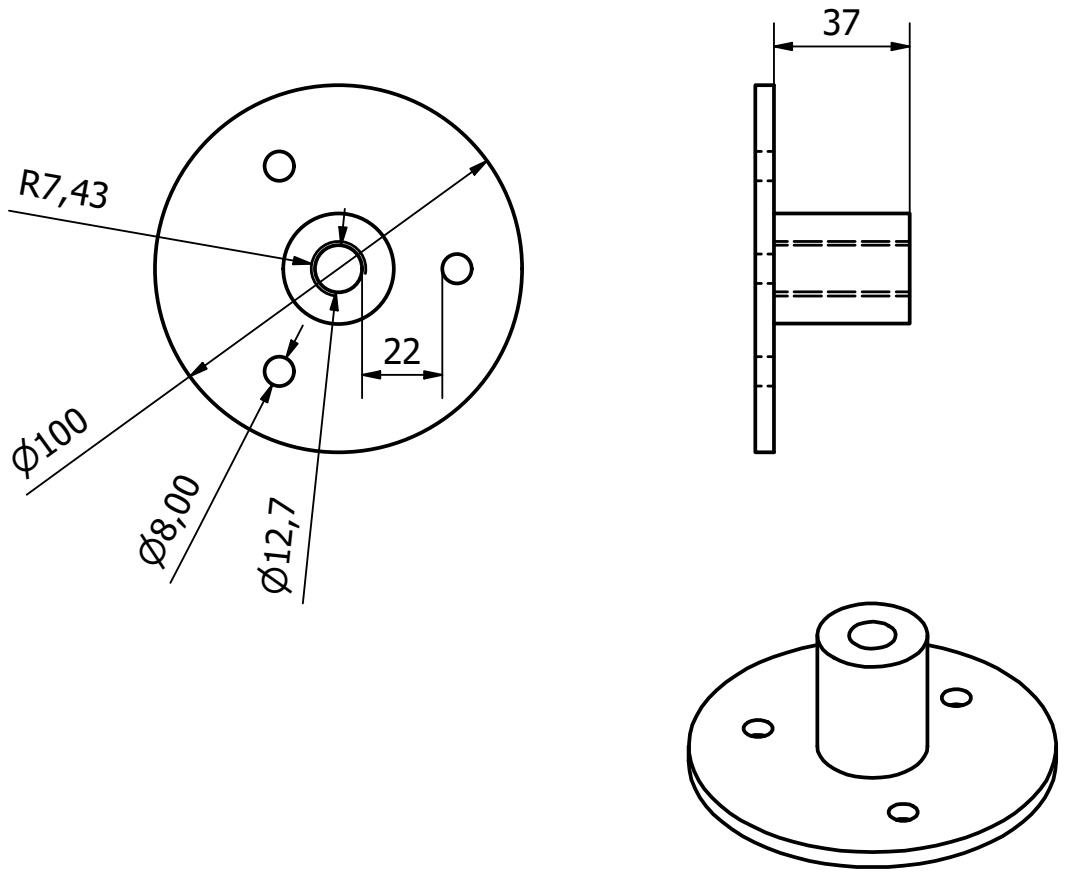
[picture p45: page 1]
Test Flange; Designed by; Checked by; Approved by; Date

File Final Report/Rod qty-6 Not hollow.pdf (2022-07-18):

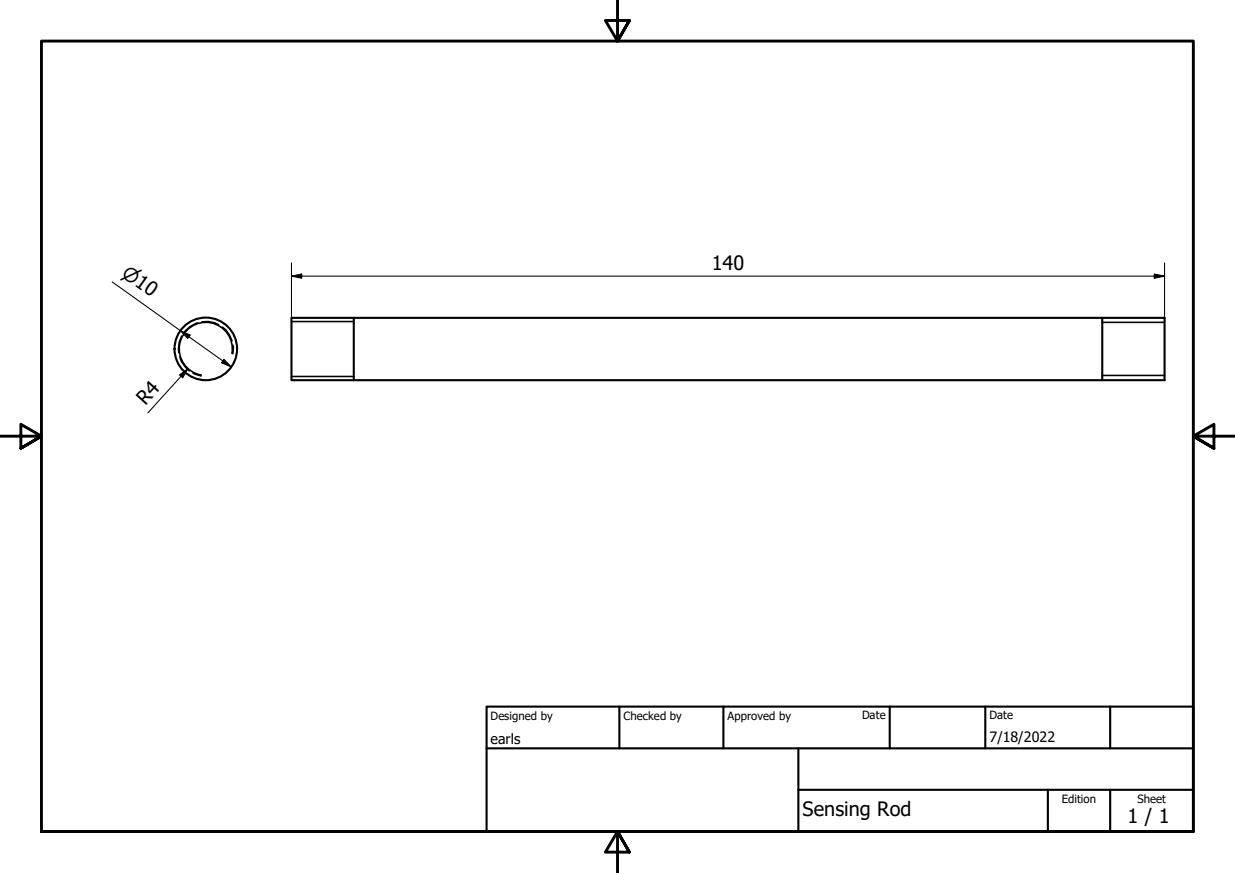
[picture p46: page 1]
Sensing Rod; Designed by; Checked by; Approved by; Date

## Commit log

2022-06-22 reorganize and add pcb files
2022-06-29 f(pcb) add modbus circuit
2022-06-30 Mechanical Design
    "Assemby 3" is the final Stewart Platform assembly to achieve 6 degrees of freedom.
    [Adapter shaft.ipt, Assembly1.0006.iam, Assembly1.iam, Assembly2.0003.iam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]
2022-07-04 Updated CAD
    [Assembly2.0003.iam, Assembly2.0004.iam, Assembly2.iam, Assemby 3.0006.iam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]
2022-07-07 draft complete pcb
2022-07-07 add pcb
2022-08-16 Flowchart done
2022-08-17 Change
    from "tunnel's mounting sting" to "tunnel's test section"
2022-08-17 Equation
    I hope you meant "P" is the static pressure
2022-08-18 Servo angles
    Results from simulation
2022-08-24 f(PCB) redesign for fab
    [BOM_PCB_stewart-platform.csv]
2022-08-24 f(PCB) switch to non standart esp32
    [BOM_PCB_stewart-platform.csv]
2022-08-24 f(PCB) modified DRC and switched diode to ss34
    [BOM_PCB_stewart-platform.csv]
2022-08-24 f(PCB) remove redundant i2c interface
2022-08-25 f(pcb) finalizing pcb and replace power supply
2022-08-29 f(PCB) switch rs485 to uart2 pins
2022-09-12 Smoke generator
    [Smoke generator.0001.ipt, Smoke generator.ipt]
2022-09-12 f(HMI) standard sender queue f(firmware) receive servo events
2022-09-12 f(firmware) write servo positions
2022-09-20 CAD Smoke emitter
    [Pitot Tube.ipt, Streamline smoke.ipt, Wind Tunnel Assembly 1 with pitot.idw, Wind Tunnel Assembly 1.0001.iam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]
2022-09-23 fix(firmware) servo attachment order and case bug f(HMI) unit testing and check for errors in calculate method
2022-09-29 CAD Update
    [Assembly2.0001.iam, Assembly2.iam, Ideation.ipt, Smoke visualization device.0004.ipt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]
2022-10-05 Smoke visualizer bottom updated
    [Smoke visualization bottom.0001.ipt, Smoke visualization bottom.0002.ipt, Smoke visualization bottom.ipt, Smoke visualization bottom.stl]
2022-10-05 Smoke connector
    [Smoke connector.ipt, Smoke connector.stl]
2022-10-10 CAD Additions
    [Assembly1.0001.iam, Assembly1.iam, Assembly2.0001.iam, Assembly2.0002.dwg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]
2022-11-11 f(firmware) new assembly f(HMI) force transformation
2022-11-24 add live charts calibration and more
2022-11-28 move pitot to servo task
2022-12-01 Pitot tube
    Pitot tube Pa readings | Smoke Connector
    [Smoke connector ready.stl, Smoke connector.0003.ipt, Smoke connector.ipt]
2022-12-05 Pressure Measurement
    Pitot at the test section
2022-12-11 Smoke visualization
    [Assembly1.dwg]
2022-12-11 Rake and pipe assembly
2022-12-17 f(HMI) individualized calibration
2022-12-19 Abstract
    Inclusion of smoke visualization assembly
